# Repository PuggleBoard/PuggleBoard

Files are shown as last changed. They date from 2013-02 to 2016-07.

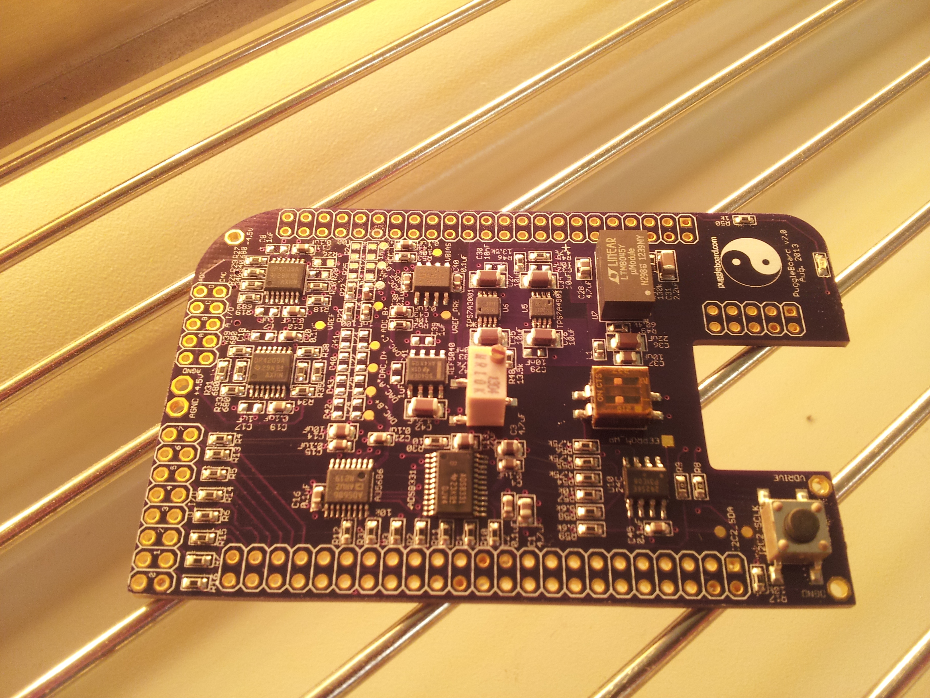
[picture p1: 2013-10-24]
art/PuggleBoard_2v1_reflow.jpg

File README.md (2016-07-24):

PuggleBoard
===

Note: The PuggleBoard project is no longer under active development as of 06/2016. For alternative low-cost electrophysiology options, please see <a href="http://github.com/rtxi/rtxi">RTXI</a> or <a href="http://github.com/open-ephys/">Open-Ephys</a>.

The [PuggleBoard] (http://puggleboard.com/) is an I/O interface that plugs into the BeagleBone Black's expansion headers and is controlled by <a href="https://github.com/PuggleBoard/PuggleDriver">PuggleDriver</a>.

To get started, please refer to the <a href="https://github.com/PuggleBoard/PuggleBoard/wiki">wiki</a>. If you encounter any trouble or have any questions, post them to the <a href="https://github.com/PuggleBoard/PuggleBoard/issues">issues section</a> and we'll help get you started.

Visit visit the <a href="http://puggleboard.com">Puggleboard</a> site for more information on Puggle and it's hardware/software components.

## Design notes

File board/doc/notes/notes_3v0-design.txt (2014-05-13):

I spoke with Edgar Brown about revision 2.1 and he gave a lot of helpful advice. Here is the summary of his comments.

1. [E] Use matched resistor arrays instead of discrete components

	> This is especially true for the onboard analog input/output stages.
	> Saves space
	> Individual resistors will introduce large mismatches unless you use relatively high tolerances. 
	> You can get 2% resistor arrays that have matched resistors down to 0.1% (these circuits are sensitive to matching, not to specific resistor values). 
	> Note that a 1% mismatch in that circuit can introduce a 300+ count mismatch on the output, more than twice the offset of the DAC itself. Not necessarily a problem, but something to keep in mind when using 16-bit DACs.
    > I see that the space is rather restricted, some resistor arrays (such as this one: http://www.digikey.com/product-detail/en/EXB-38V330JV/Y9330TR-ND/256513 ) could be used to open up some space around the connectors. One of those takes half the space than four 0603’s and are not that hard to solder.

2. [E] I am not sure of the specifics of the AD5686 or of the application, but in many bio-applications it is desirable to have simultaneously sampling ADCs and DACs (it considerably simplifies signal processing). I believe the LDAC line can serve this purpose, which here you have disabled.

	> Yes, that is the purpose of LDAC. We should dedicate an extra PRU pin to control LDAC. 
	> The ADS8331, however, does not allow simultaneous sampling. I'm not quite sure how this would simplify signal processing. 

3. [E] The schematics are harder to read than necessary as you used generic boxes for common items such as operational amplifiers. What is normally a quick pattern recognition task becomes a bit mental puzzle. It took me a minute to recognize a simple analog level shifter.

	> I will replace strange boxes with standard opamp symbols
	
X4. [E] Regarding the reset button. Why a reset button at all? it takes space and you would probably do it programmatically anyway. I am guessing that both the ADC and the DA can be reset via the SPI bus. If not a connection to a free I/O pin takes less space.

	> This is important to have for the sake of biologists. For instance, say they start inadvertantly electrolesioning an animal because they put a DC offset on a stimulating electrode. They panic. I want there to be a real button they can hit to make bad things stop. I actually use the reset switch quite a lot on Arduino boards, for instance.
	
?5. [E] I see no connection to the End of Conversion in the ADC. I am not sure if you need it, but it is normally required to drive the ADC at maximum speed.

	> My understanding is that this is used to signal an interupt indicating a conversion has taken place and the host processor can begin pulling data.
	> We have a fixed delay for conversions, so I'm not sure this will be helpful for us. Could be wrong here.
	
6. [E] What is the purpose of S1? wouldn’t it make more sense to select the address either programmatically or have it fixed for the board? That switch seems to take a lot of space for very little functionality. If the purpose is to be able to connect multiple boards together, I am not sure that your configuration of IO lines allows for that. A set of jumpers (resistor locations with 0-ohm resistors) could achieve the same thing with less space. (Also note that the parallel of R59 and R58 in multiple boards would quickly drive the I2C lines out of spec).

	> This is a requirement to produce a BeagleBoard 'cape' that conforms to BeagleBoard design requirments. Each BB is allowed up to four capes, defined by the position of the DIP switch, which must be selectable by the user. You are right that this could be done with solder joints or jumpers, but this is not the standard for other capes. Jumpers are a reasonable idea, but how much space will it really save?
	> In regard to R59/58 -- yes, but this again is what is recommended by BeagleBoard.org. Only 4 capes are allowed so I don't think that will be enough to load down the I2C line to the point where it no longer works.
	> Although our boards are not daisy-chainable, we want our board to conform to these requirments so it can be used with unrelated projects that use nonoverlapping GPIO pins -- e.g. a Wirless module or video capture.

7. [E]  Avoid connecting two pads directly, like pins 21 & 22 in U2. It makes it harder to spot soldering errors. Even when an outside company solders it, I have had to thoroughly inspect very carefully professionally soldered boards pin by pin to find soldering mistakes.

    > Good idea, will do.

8. [E] - Did you draw the INTAN wires by hand? Or is there some Eagle tool to match trace lengths now?
    
    > There is a tool. Its called the 'meander' tool.

9. [E] U7 is a major source of noise on top of AGND.I have to look at that IC more carefully, but I have a hunch that that is your main noise source on the whole board. The way AGND is organized around that IC guarantees that the noise it generates will find its way into all of the circuity.

    > [J] agree the U7 is certainly the most difficult to deal with from a design point. We need it to produce a negative power rail because we don't want the board to rely on a benchtop supply or batteries. I was really careful on the layout for that component (i.e. following the datasheet and eval board), and we actually do not see its switching transients leaking into the rest of the circuit in the current config. Of course, it could be producing less obviously correlated noise. I would really like to understand why this AGND pattern is no good. I am honestly at a loss sometimes with grounding patterns

10. [J] Our biggest, most obvious problem is definitely interference from the digital buses onto analog lines. 

    > [E] The connection of AGND to pin one on the right-side beaglebone connector might be the source of much of your digital noise. That creates a ground path for beaglebone digital signals through the AGND of your board. That is part of having just a single ‘point’ of connection between grounds. For space sake, and to reduce the adverse effects that simply disconnecting that ground might have on the switching noise from U7, It would be ok to have U7 in a separate GND domain directly connected to the beagle bone, with only L1 and C37 bridging the gap.

11. [E] I noticed that you have no anti-aliasing filters in place. You basically put a single pole at 1.6MHz for DACs that, I assume, will be sampling at a maximum of 125kS/s (this is already higher than the 1.25MHz bandwidth coming out of the op-amps). I know you are probably going for some flexibility, but this actually goes against your noise performance. You should at the very least move those filters down to 60kHz or so which should remove most of the problematic bandwidth. It might be advisable to change the amplifier architecture to incorporate 2-nd or 3-rd order filters there.

    > [J] Yeah, this is almost certainly true. At least the pole of the output filter should be below the opamp bandwidth...
    > One reason I don't want to put the pole all the way down at 60 kHz is that this prevents the user from generating fast square waves with the DAC. I suppose this is what the extra digital lines are for though?

12. Your switching frequency for the voltage converter is in the 700kHz range, which is already outside of the bandwidth of interest, but it can be easily aliased inside by lack of filtering (thus making it unrecognizable in a digital trace).

    > [J] Certainly true. I think this, and point 11, indicate that we need a lower frequency cutoff for the AA filtering

13. [E] I noticed that your ADC/DAC connector has no intervening grounds in it. Not much of a problem for the low-impedance DAC lines, but it can be an issue for the ADCs. The most common way to wire those is to have a row of grounds and a row of ‘active’ signals. That way the flat cable has a ground wire separating every signal from each other. As you have it, any noise in the DAC lines will capacitively and inductively couple back into the ADC lines. Add that to the lack of filtering and that is a clear path for noise.

    > [J] This is an easy change and we will certainly implement it. 

14. [E] Place the capacitors C5, C6, C9, C12 close to the ADC itself. That way any injected noise in those traces will have a direct path to the common node of the ADC itself. Alternatively connect the “COM” line from the ADC close to those capacitor's gnd, with a trace that closely follows those inputs.

    > [J] Thank you. This is the type of thing I never would have figured out on my own. Will certainly implement.

15. Replace the AD8032 and REF5040 with an MSOP package

    > Make sure to update BOM with (DK: AD8032ARMZ-REEL7CT-ND, MPN: AD8032ARMZ-REEL7)

16. You should have a mini-BNC or BNC sync out connection using a 50-ohm line driver or several paralled schmitt triggs with a characteristic 50-ohm out impedance. This will allow you to sync slave boards (e.g. the 64 channel version).

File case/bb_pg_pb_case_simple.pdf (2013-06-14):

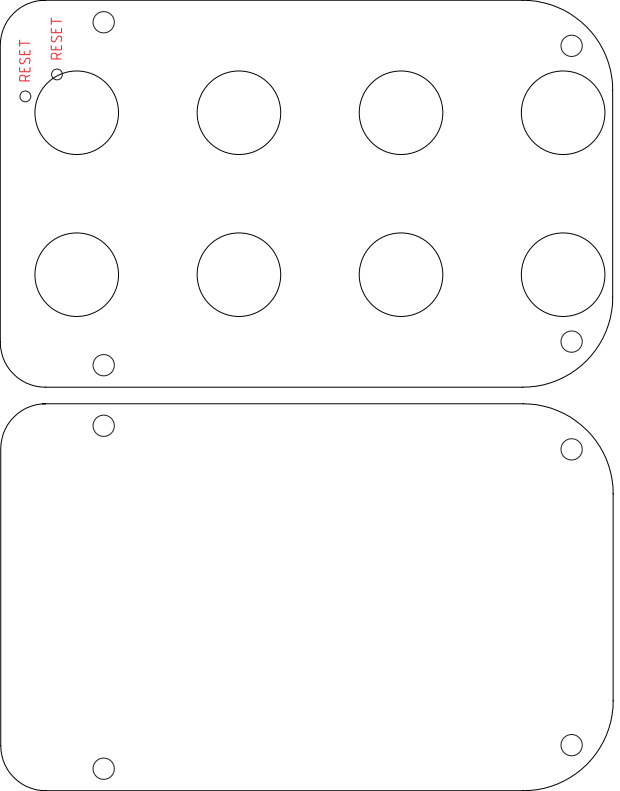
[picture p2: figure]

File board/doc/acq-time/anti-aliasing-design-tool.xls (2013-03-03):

 |  |  |  | Anti-Aliasing Filter Tool
Enter Converter Resolution: | 16 | bits
Enter Sample Rate: | 250000 | Hz
Nyquist Frequency: | 125000 | Hz
Enter Signal Bandwidth: | 20000 | Hz
Required Attenuation: | -98.08 | dB
Number of Filter Poles: | 4
Freq Factor | Frequency | Gain | Required Attenuation
0.0009765625 | 19.53125 | 0 | -98.08
0.001953125 | 39.0625 | 0 | -98.08
0.00390625 | 78.125 | 0 | -98.08
0.0078125 | 156.25 | 0 | -98.08
0.015625 | 312.5 | 0 | -98.08
0.03125 | 625 | 0 | -98.08
0.0625 | 1250 | 0 | -98.08
0.125 | 2500 | 0 | -98.08
0.25 | 5000 | 0 | -98.08
0.5 | 10000 | 0 | -98.08
1 | 20000 | 0 | -98.08
2 | 40000 | -24 | -98.08
4 | 80000 | -48 | -98.08
8 | 160000 | -72 | -98.08
16 | 320000 | -96 | -98.08
32 | 640000 | -120 | -98.08
64 | 1280000 | -144 | -98.08
128 | 2560000 | -168 | -98.08
256 | 5120000 | -192 | -98.08
512 | 10240000 | -216 | -98.08
1024 | 20480000 | -240 | -98.08
 | 250019.5312 | 0 | -98.08
 | 250039.0625 | 0 | -98.08
 | 250078.125 | 0 | -98.08
 | 250156.25 | 0 | -98.08
 | 250312.5 | 0 | -98.08
 | 250625 | 0 | -98.08
 | 251250 | 0 | -98.08
 | 252500 | 0 | -98.08
 | 255000 | 0 | -98.08
 | 260000 | 0 | -98.08
 | 270000 | 0 | -98.08
 | 290000 | -24 | -98.08
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

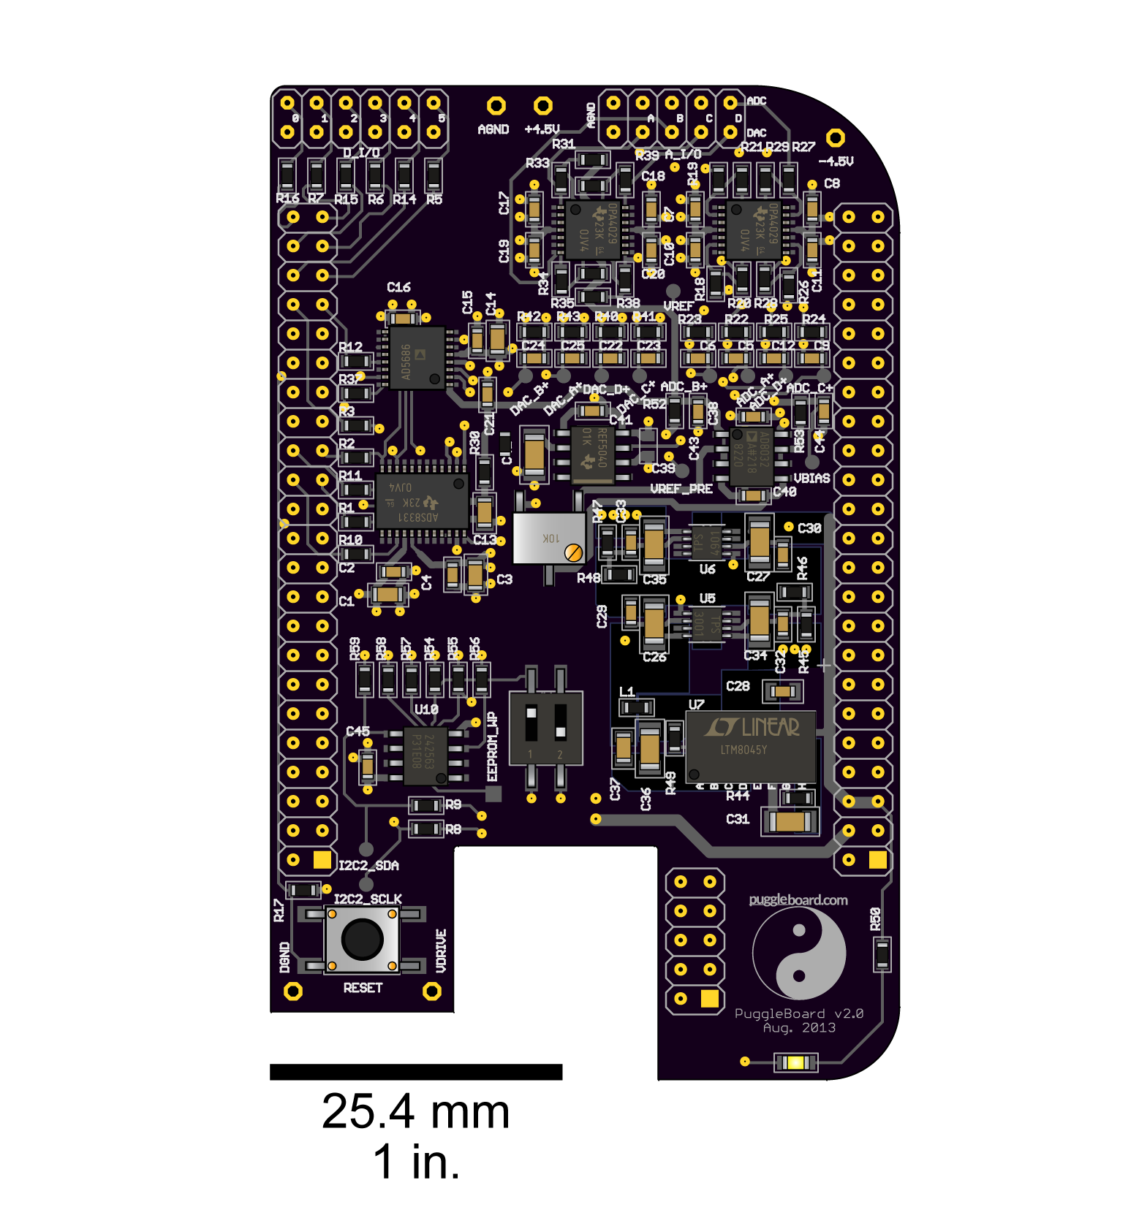
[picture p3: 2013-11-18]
art/PuggleBoard_2v1-02-01.png

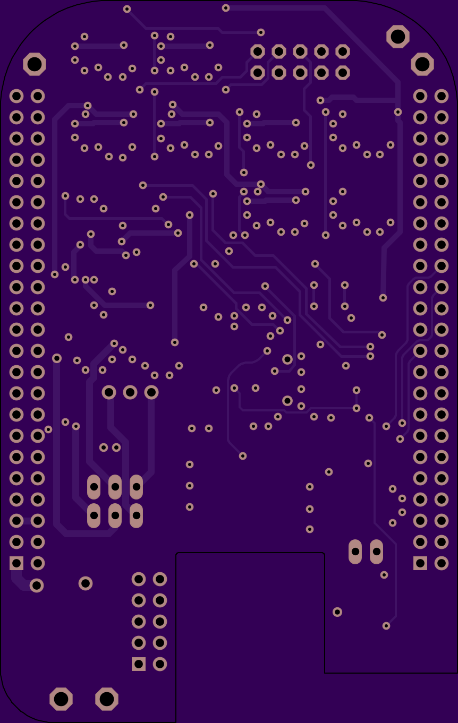
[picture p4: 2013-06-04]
art/PuggleBoard_OSHPark_Bottom.png

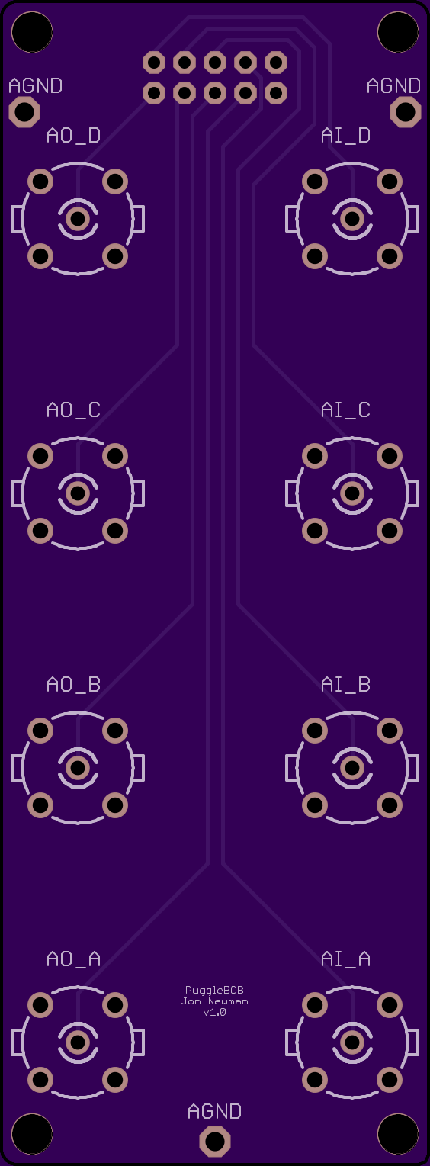
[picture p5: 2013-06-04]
bobs/bnc-bob/art/PuggleBOB_OSHPark_Top.png

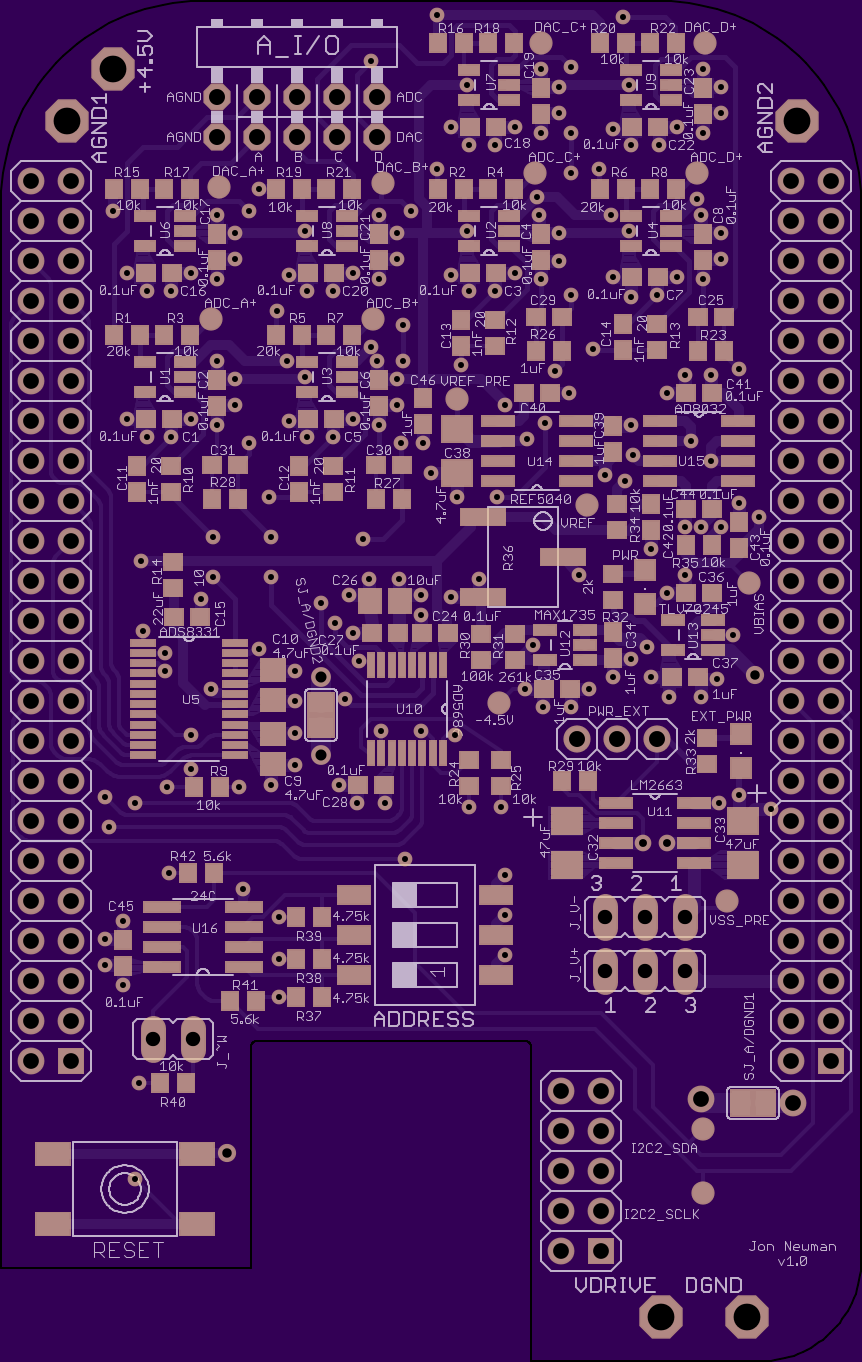
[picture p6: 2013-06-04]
art/PuggleBoard_OSHPark_Top.png

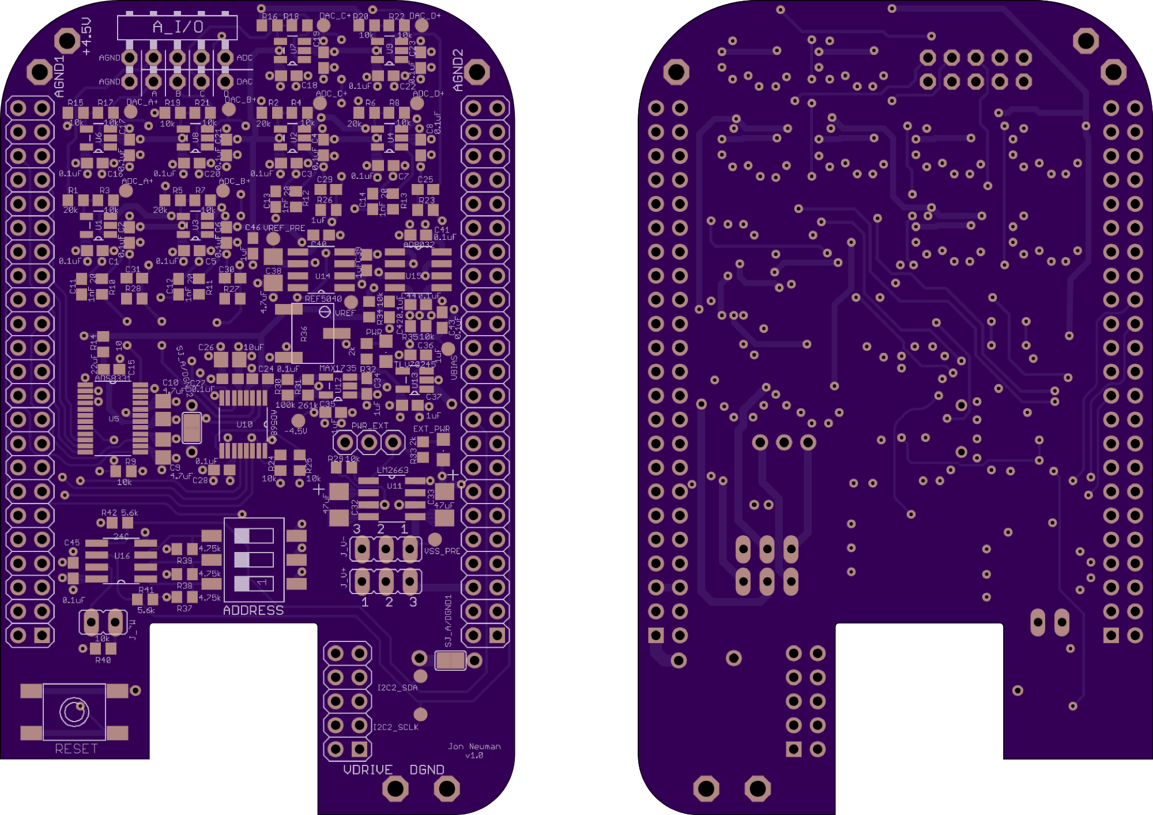
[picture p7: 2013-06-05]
art/PuggleBoard_OSHPark.png

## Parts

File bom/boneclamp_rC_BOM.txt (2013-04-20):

------------
1. POWER 
------------

DC-DC INVERTER (-5 VOLT OUTPUT):
--------------------------------
U1    N.A.    296-18729-1-ND    10-SON        1    DIGI-KEY    
C1    0.1uF   445-7558-1-ND     0805          1    DIGI-KEY    
C2    0.22uF  399-8053-1-ND     0805          1    DIGI-KEY  
C3    10pF    399-5567-1-ND     0805          1    DIGI-KEY    
C4    10uF    445-6857-1-ND     0805          1    DIGI-KEY  
C5    4.7uF   445-5973-1-ND     0805          4    DIGI-KEY   
C6    10nF    399-9154-1-ND     0805          1    DIGI-KEY  
C7    22nF    399-1163-1-ND     0805          1    DIGI-KEY  
C8    4.7nF   399-1155-1-ND     0805          1    DIGI-KEY  
R1    100k    P100KCCT-ND       0805          1    DIGI-KEY   
R2    150k    P150KCCT-ND       0805          1    DIGI-KEY  
R3    750k    P750KCCT-ND       0805          1    DIGI-KEY   
D1    N.A.    SL02-GS08CT-ND    DO-219AB      1    DIGI-KEY
L1    4.7uH   445-3235-1-ND     N.A.          1    DIGI-KEY  

DC-DC SWITCHED CAPACITOR VOLTAGE INVERTER (-VIN OUTPUT):
-----------------------------------------------------------
U1    N.A.    LM2663M/NOPB-ND PSOP-8          1    DIGI-KEY
C1,2  47uF    399-4714-1-ND   1206            2    DIGI-KEY

-5 VOLT LDO REGULATOR:
----------------------
U1    N.A.    LT1964ES5-5#TRMPBFCT-ND    10-SON      1    DIGI-KEY  
C1    1uF     399-1284-1-ND     0805          1    DIGI-KEY  
C2    10uF    445-6857-1-ND     0805          1    DIGI-KEY  
C3    10nF    399-9154-1-ND     0805          1     DIGI-KEY  

+4.75 VOLT LDO REGULATOR:
-------------------------
U1    N.A     296-28110-1-ND    SOT23-5       1   DIGI-KEY
C1,2  1uF     399-1284-1-ND     0805          2    DIGI-KEY  
L     N.A.    350-2044-1-ND     0805          1   DIGI-KEY

----------------------
2. SIGNAL CONDITIONING
----------------------

VADC BIAS:
----------
U1,2    N.A     AD8022ARZ-ND      8SOIC       2   DIGI-KEY

VDAC BIAS:
----------
U1,2    N.A     AD8022ARZ-ND      8SOIC       2   DIGI-KEY

----------------------
2. SIGNAL CONVERSION
----------------------

ADC:
----
C1,2    445-1316-1-ND     C1608X7R1E104K080AA   0603    DIGI-KEY

R1,2 	47k		A103211CT-ND	0805			2	DIGI-KEY

-----------------------
4. BEAGLEBONE INTERFACE
-----------------------

TEST1-4 N.A.    350-2041-1-ND 0805  4   DIGI-KEY
R1-4    2k      

RESET  N.A.     450-1129-ND     1   DIGI-KEY

----------------------
5. PROTOTYPE SUPPLIES
----------------------

BREAKOUT BOARDS
A1    N.A.    PA0063            20-QFN to DIP       1    PROTO-ADVANTAGE
A2    N.A.    PA0034            TSSOP-16 to DIP     1    PROTO-ADVANTAGE
A3    N.A.    PA0191            TSSOP-10 to DIP     1    PROTO-ADVANTAGE
A4    N.A.    PA0180            TSOT-6 to DIP       1    PROTO-ADVANTAGE

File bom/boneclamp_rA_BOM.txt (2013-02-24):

Jonathan P Newman
jnewman6 snail gatech dot edu

Revisions:
2013 01 24

********************************************************************************
                    T I N Y - C L A M P  C A P E  B. O. M.
********************************************************************************

Part No.            Description             Manufac.      Digikey No.           Quantity      

INTEGRATED CIRCUITS
--
AD5754              quad DAC                Analog        AD5724RBREZ-ND        1             
AD7656YSTZ-1        quad ADC                Analog        AD7656YSTZ-1-ND       1             
ADR421              2.5 Vref                Analog        ADR421BR-REEL7CT-ND   2             

PASSIVE COMPONENTS
--
44WR10KLFT7         10K Trimmer                 Bourns        987-1046-2-ND     x

for voltage refs:
10k trimmer
15k resistor
10 uF cap 
0.1 uF cap (2x)

for DAC:

for ADC:
1 uF cap (7x, max config, some of these are not nessesary)
2x schottky diode for supply pins (RB021VA90CT-ND)
6x 240 Ohm resistors in series with AI channels

Power reg:
2X logical level vreg for Vdig and Vanalog (dig)
+12 V vreg for Vdd (analog)
-12 V vreg for Vss (analog)
+5 V vreg for bone power (with required current ratings)

PV36P502C01B00      5K Trimmer                  Murata        490-2869-ND       1
44WR10KLFT7         10K Trimmer                 Bourns        987-1046-2-ND     x
AC07000001507JAC00  resistor, 0.15 ohm, 5%      Vishay        PPC7W.15CT-ND     1
PAC500002007FAC000  resistor, 0.2 ohm, 1%       Vishay        PPC5D.20CT-ND     1
AC07000003307JAC00  resistor, 0.33 ohm, 5%      Vishay        PPC7W.33CT-ND     1
NFR2500004707JR500  resistor, 0.47 ohm          Vishay        PPC.47ACT-ND      1
AC05000007507JAC00	resistor, 0.75 ohm					Vishay				PPC5W.75CT-ND			1
PR01000101200JR500  resistor, 120 ohm           Vishay        PPC120W-1CT-ND    1
PR01000102400JR500  resistor, 240 ohm           Vishay        PPC240W-1CT-ND    1
PR01000104700JR500  resistor, 470 ohm           Vishay        PPC470W-1CT-ND    1
PR01000101001JR500  resistor, 1 kohm            Vishay        PPC1.0KW-1CT-ND   1
PR01000101501JR500  resistor, 1.5 kohm          Vishay        PPC1.5KW-1CT-ND   1
PR01000105101JR500  resistor, 5.1 kohm          Vishay        PPC5.1KW-1CT-ND   2
PR01000101002JR500  resistor, 10 kohm           Vishay        PPC10KW-1CT-ND    2 
PR01000101004JR500  resistor, 1 Mohm            Vishay        PPC1.0MW-1CT-ND   1
RPE5C1H220J2K1Z03B  capacitor, 20 pf            Murata        490-3709-ND       1
RDEF51H104Z0K1C03B  capacitor, 100nf            Murata        490-5401-ND       4
ECA-1HM010          capacitor, 1 uF             Panasonic     P5174-ND          1  
ECA-1CM100          capacitor, 10 uF            Panasonic     P5134-ND          1
LTL1CHTBK4          On LED, 20 mA               lite-on       160-1602-ND       1

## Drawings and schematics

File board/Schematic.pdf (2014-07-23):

A

A

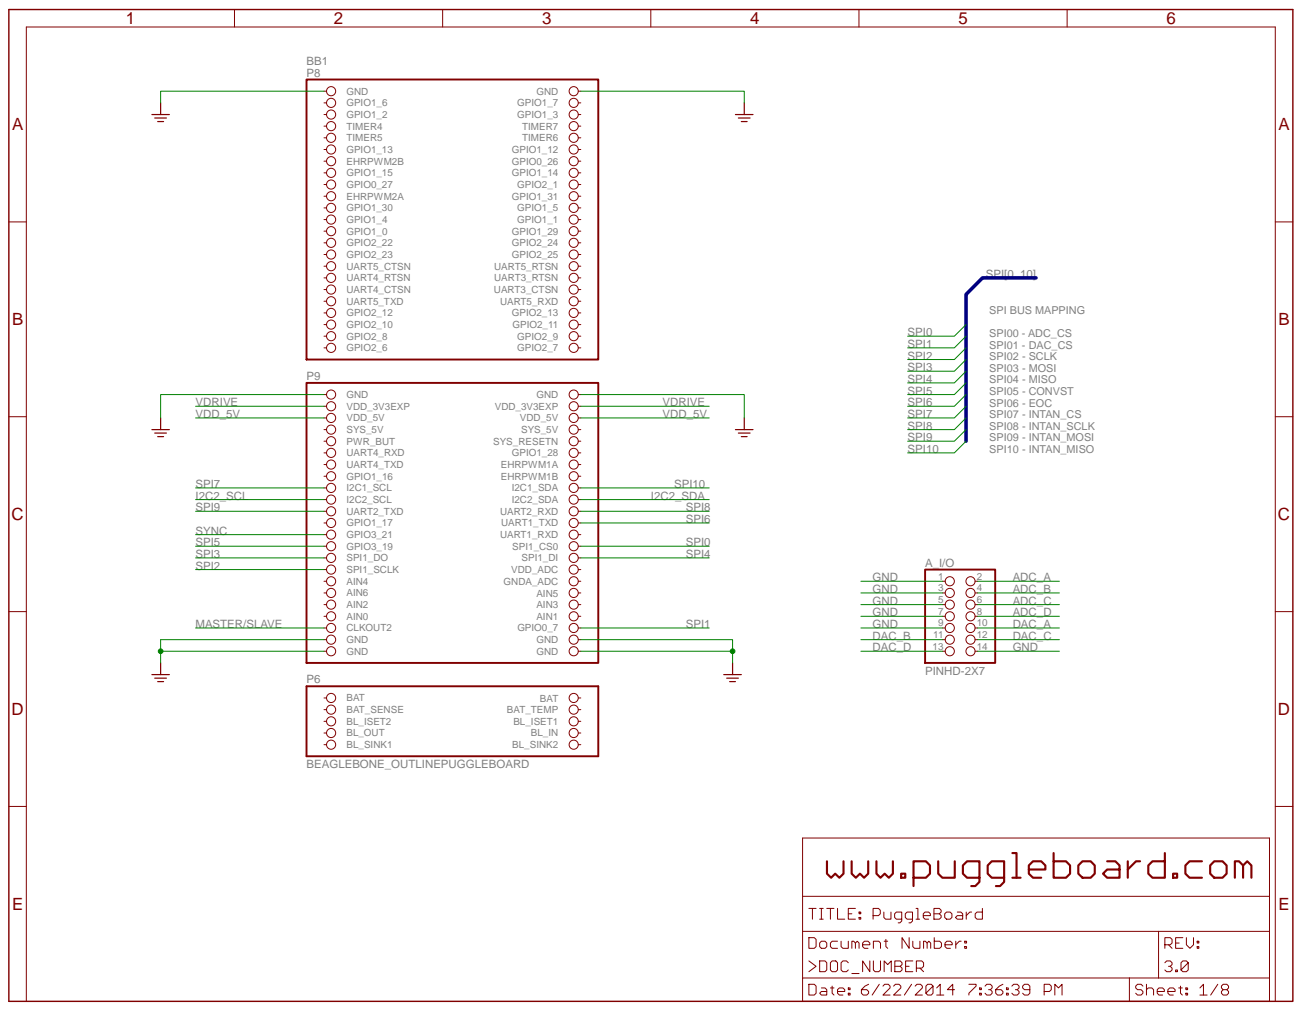
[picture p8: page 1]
SPI00 - ADC_CS SPI01 - DAC_CS SPI02 - SCLK SPI03 - MOSI SPI04 - MISO SPI05 - CONVST SPI06 - EOC SPI07 - INTAN_CS SPI08 - INTAN_SCLK SPI09 - INTAN_MOSI SPI10 - INTAN_MISO; BEAGLEBONE_OUTLINEPUGGLEBOARD; PINHD-2X7; GND; VDD_3V3EXP; VDD_5V; SYS_5V; PWR_BUT; SYS_RESETN; UART4_RXD; GPIO1_28; UART4_TXD; EHRPWM1A; GPIO1_16; EHRPWM1B; I2C1_SCL; I2C1_SDA; I2C2_SCL; I2C2_SDA; UART2_TXD; UART2_RXD; GPIO1_17; UART1_TXD; GPIO3_21; UART1_RXD; GPIO3_19; SPI1_CS0; SPI1_DO; SPI1_DI; SPI1_SCLK; VDD_ADC; AIN4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

SPI BUS MAPPING

A

A

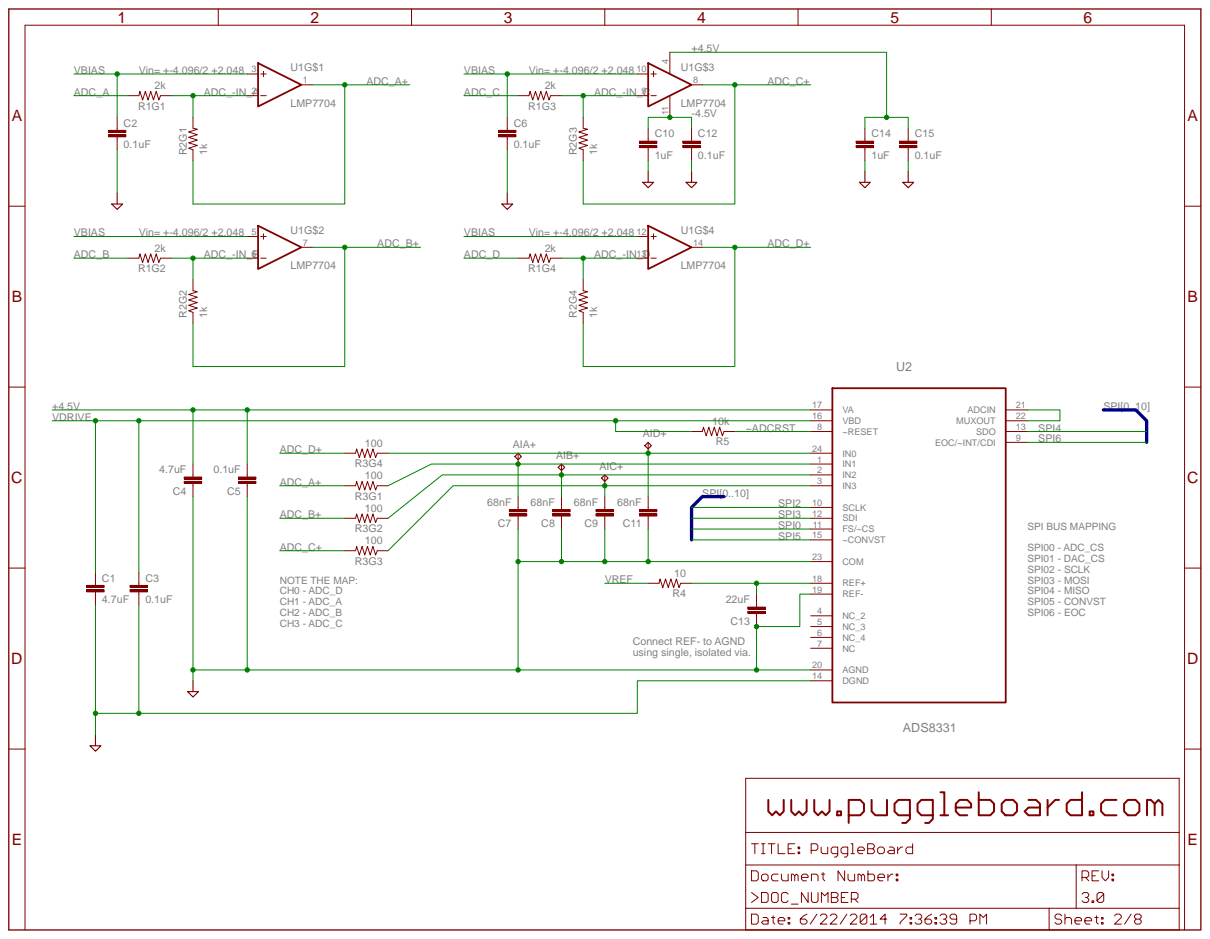
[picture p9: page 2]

Connect REF- to AGND
using single, isolated via.

A

A

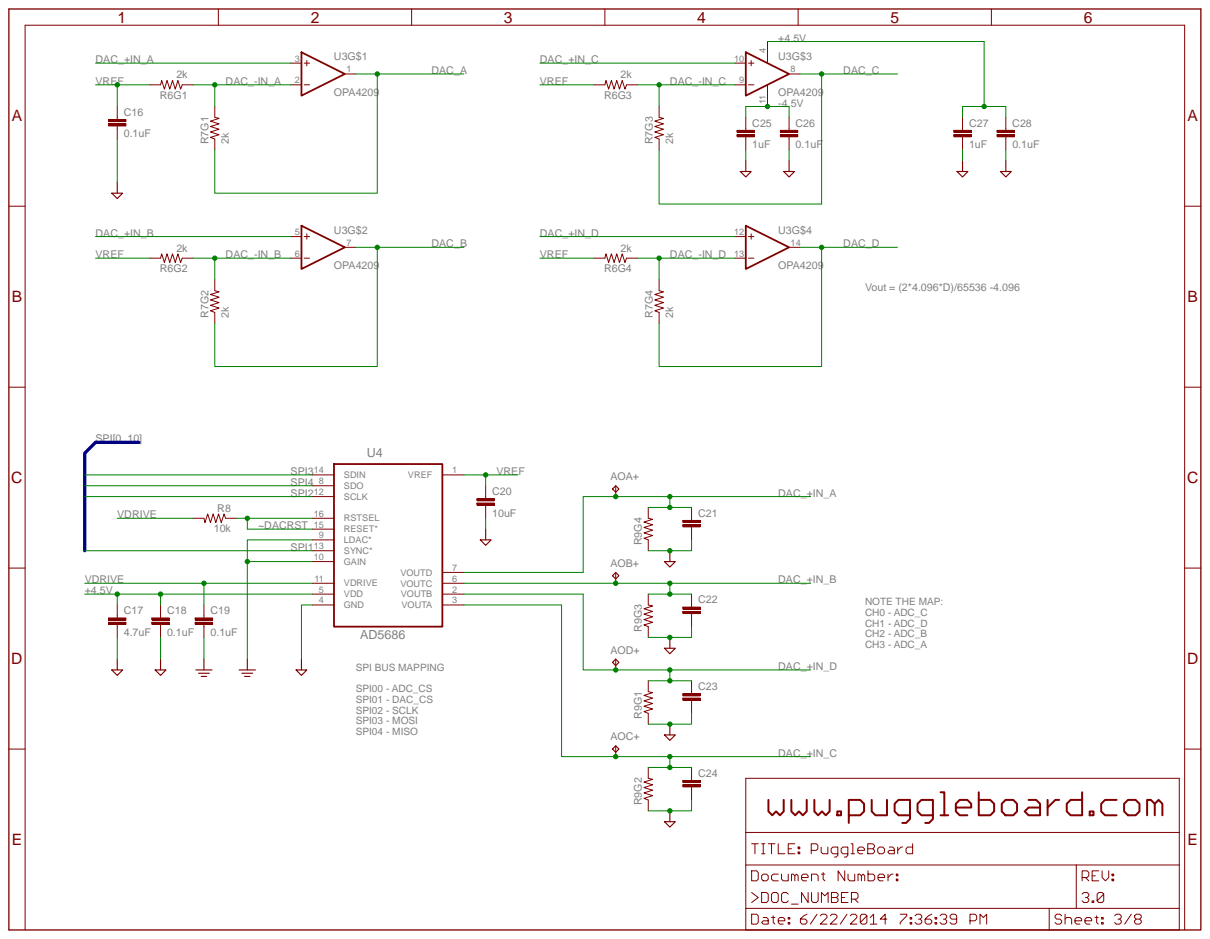
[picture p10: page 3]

A

A

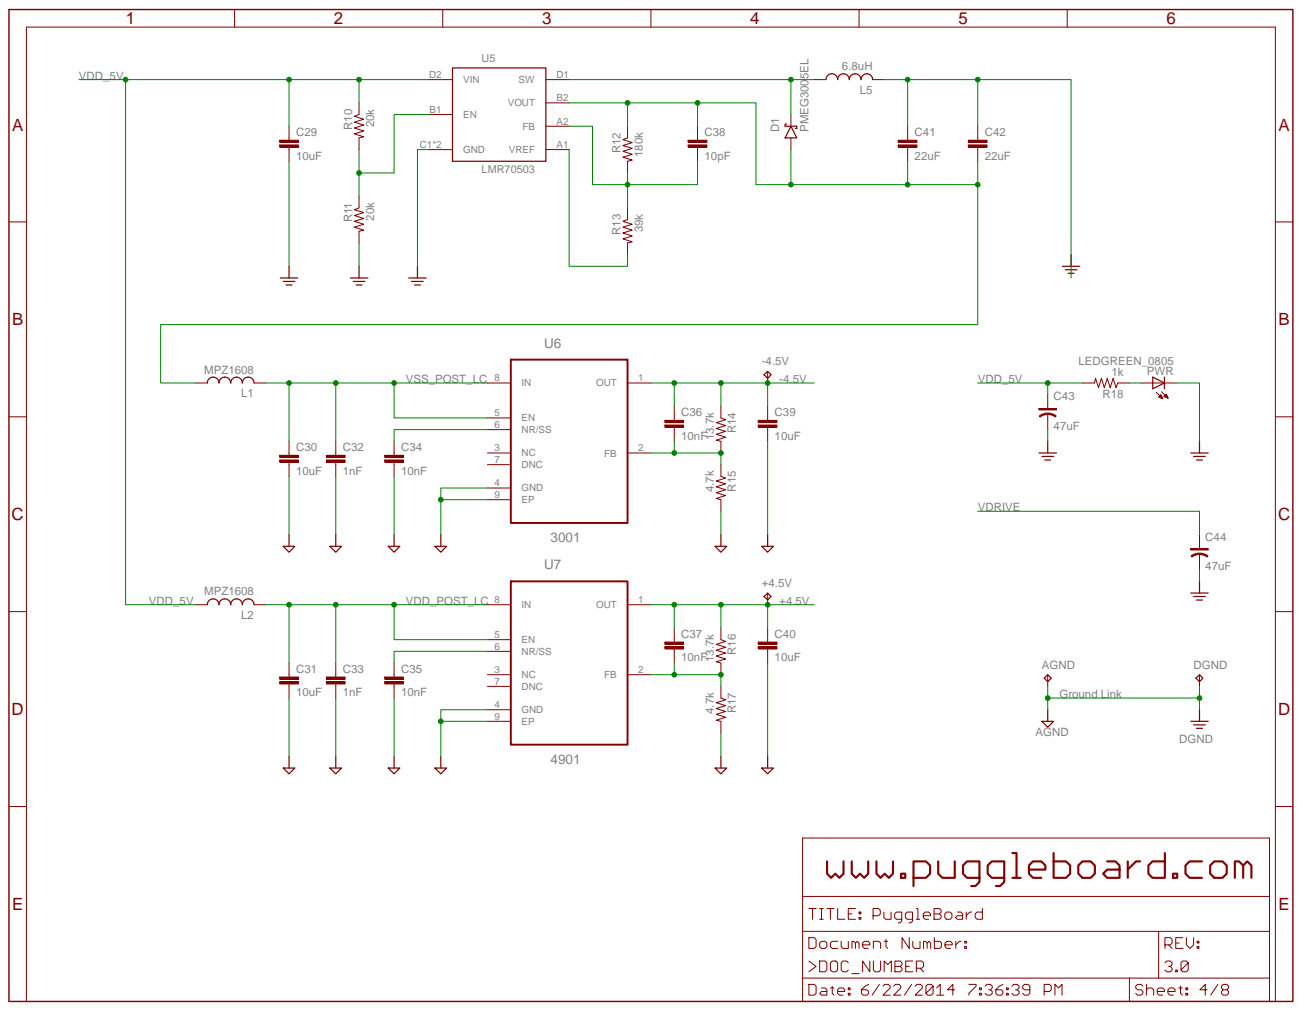
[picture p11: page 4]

A

A

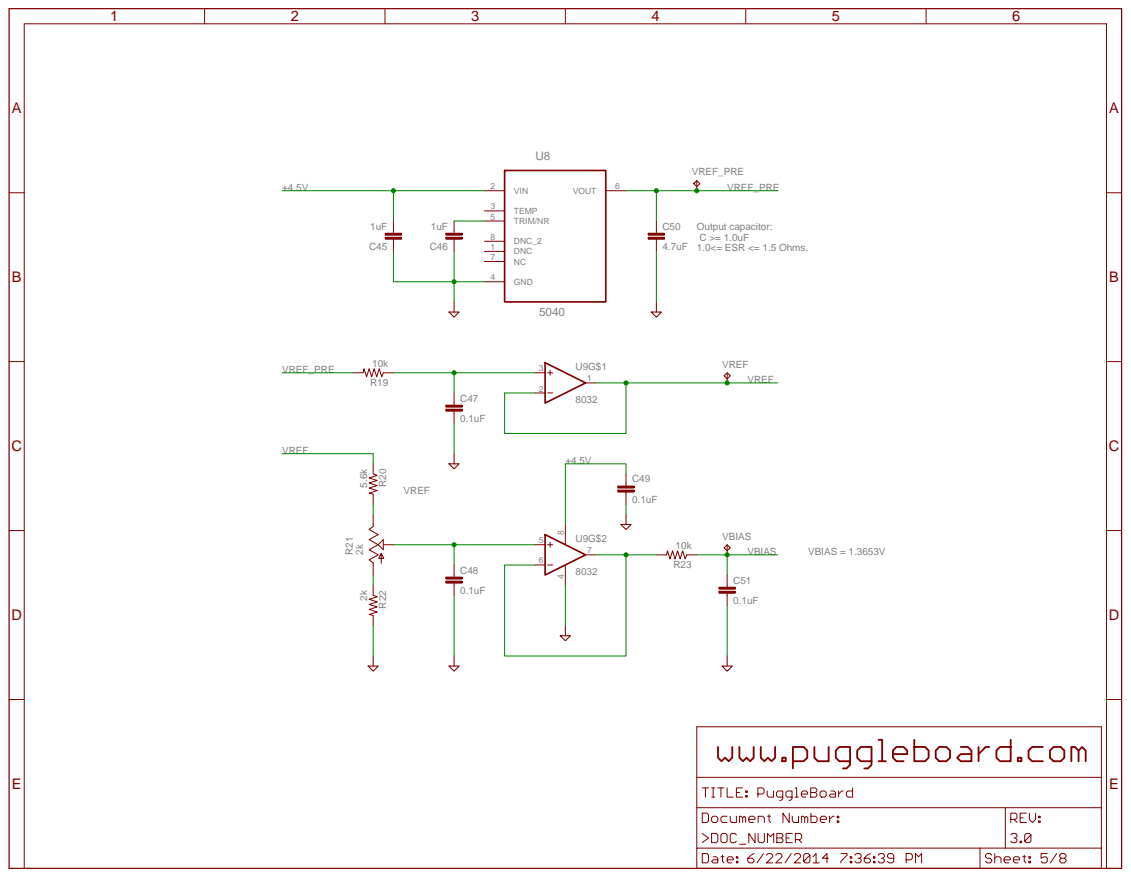
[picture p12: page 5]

A

A

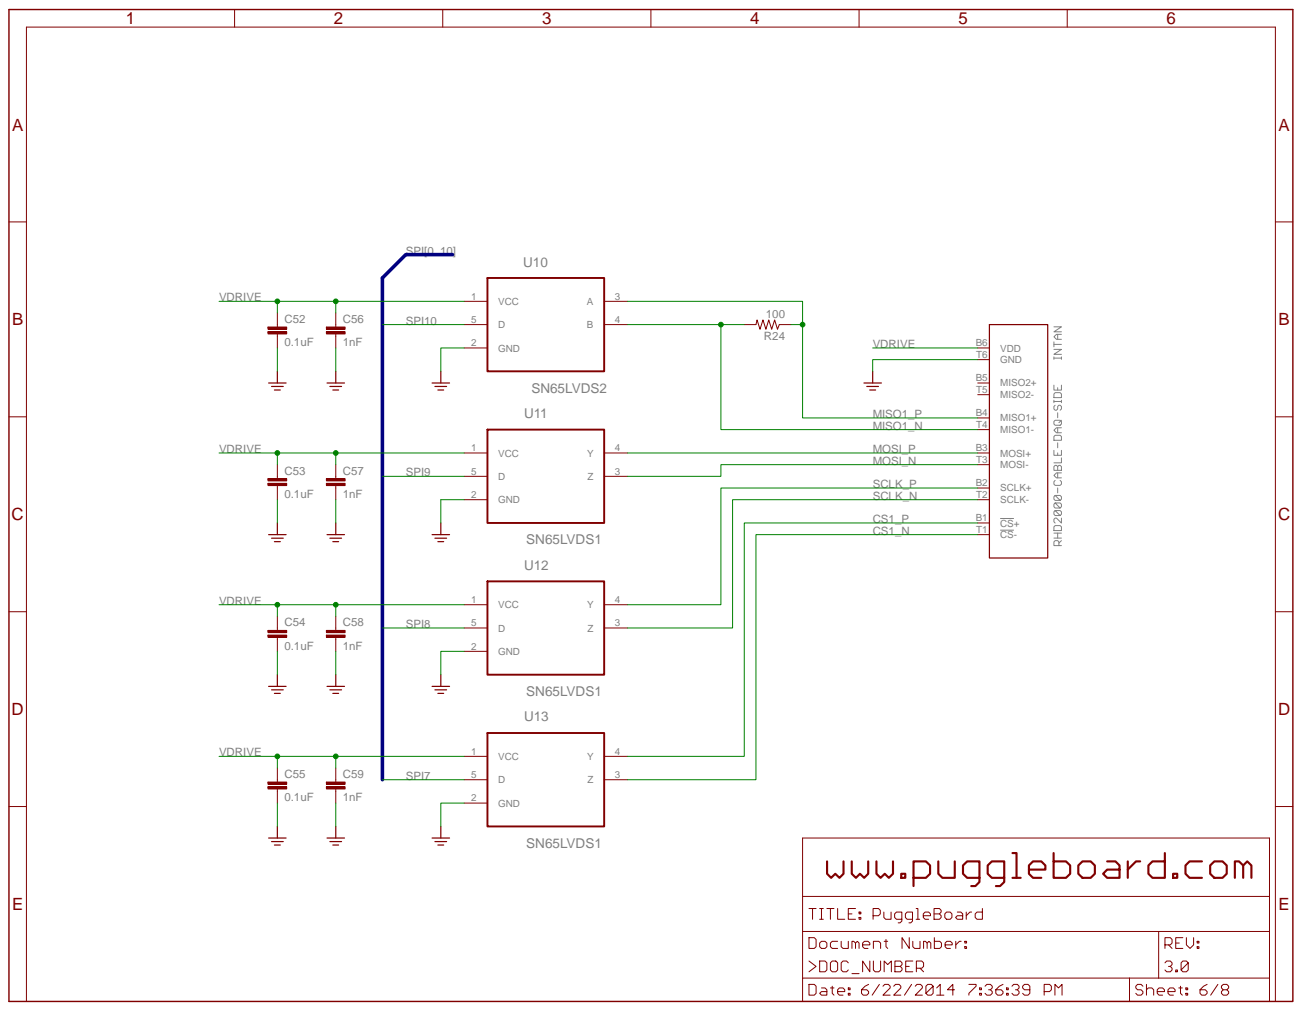
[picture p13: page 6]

A

A

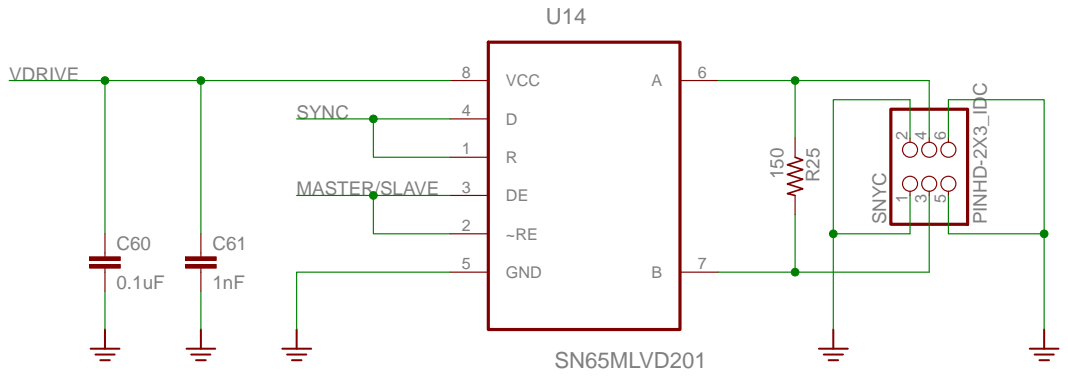
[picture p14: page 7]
SN65MLVD201; PINHD-2X3_IDC; VCC 8; GND 5; SNYC; SYNC; MASTER/SLAVE; VDRIVE

A

A

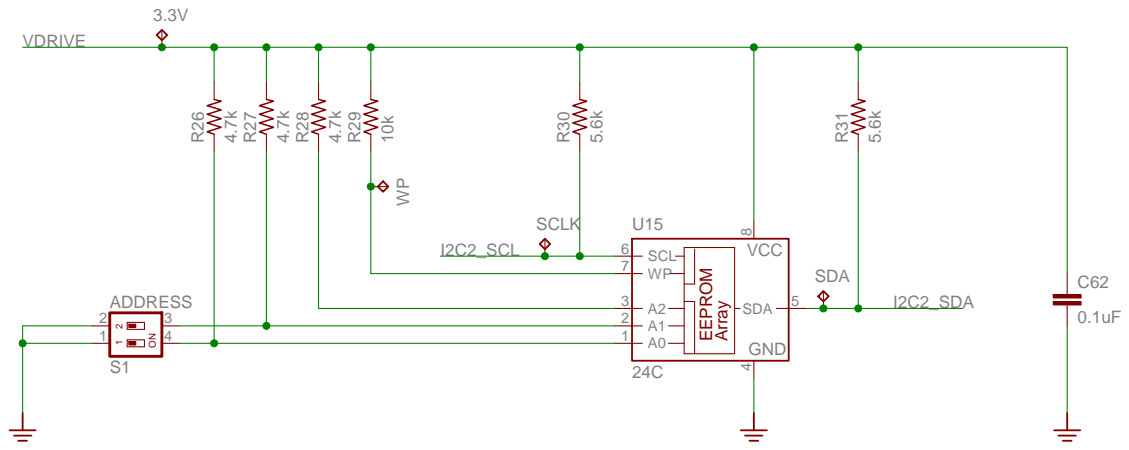
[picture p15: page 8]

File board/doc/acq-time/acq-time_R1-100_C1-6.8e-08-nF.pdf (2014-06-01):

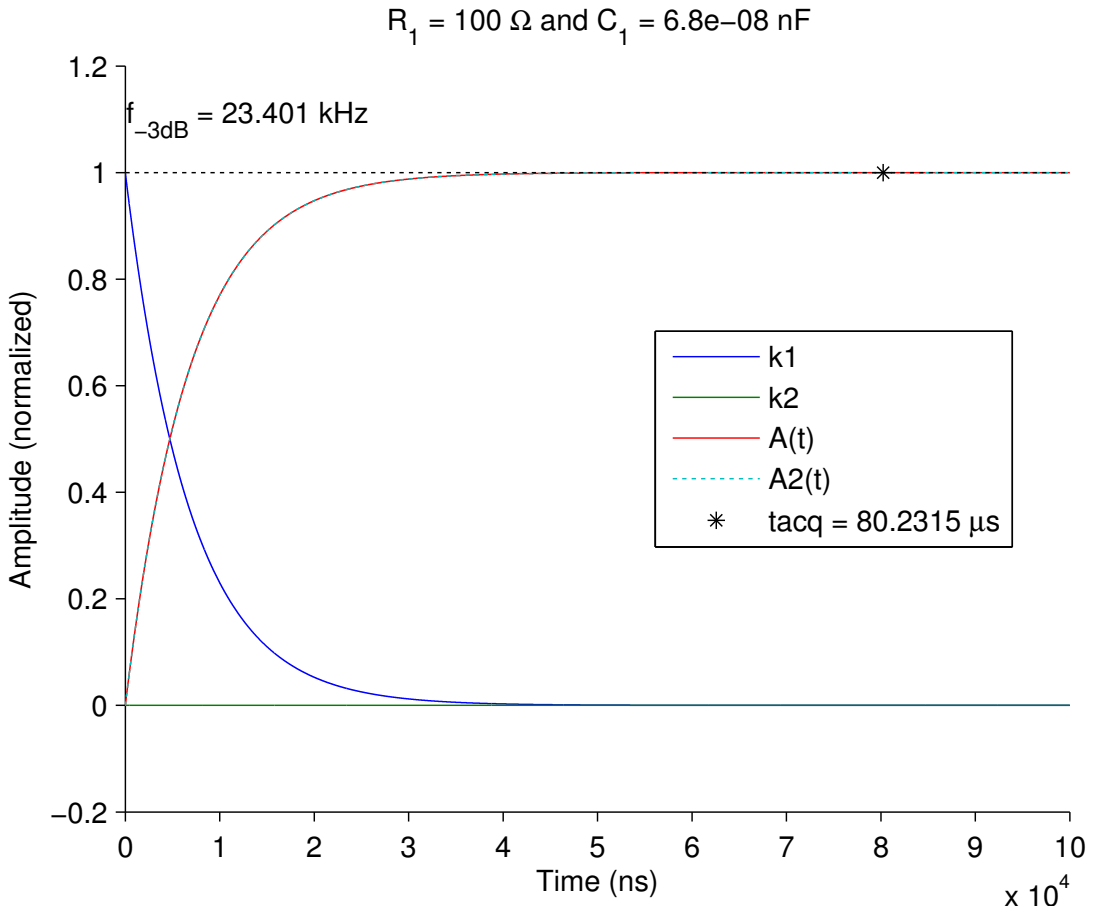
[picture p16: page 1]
Time (ns); Amplitude (normalized); = 100 Ω and C1; −3dB = 23.401 kHz; tacq = 80.2315 µs

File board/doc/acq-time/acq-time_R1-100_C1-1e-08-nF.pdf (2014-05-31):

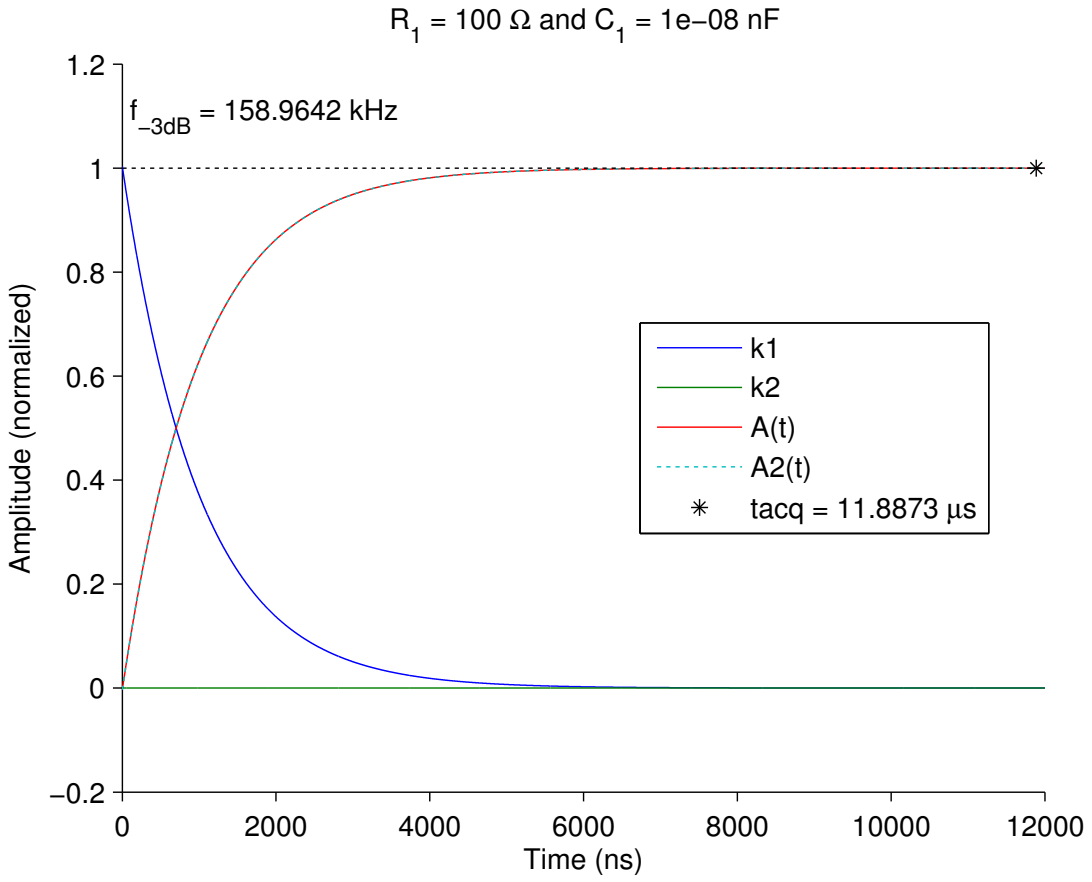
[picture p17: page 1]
Time (ns); Amplitude (normalized); = 100 Ω and C1; −3dB = 158.9642 kHz; tacq = 11.8873 µs

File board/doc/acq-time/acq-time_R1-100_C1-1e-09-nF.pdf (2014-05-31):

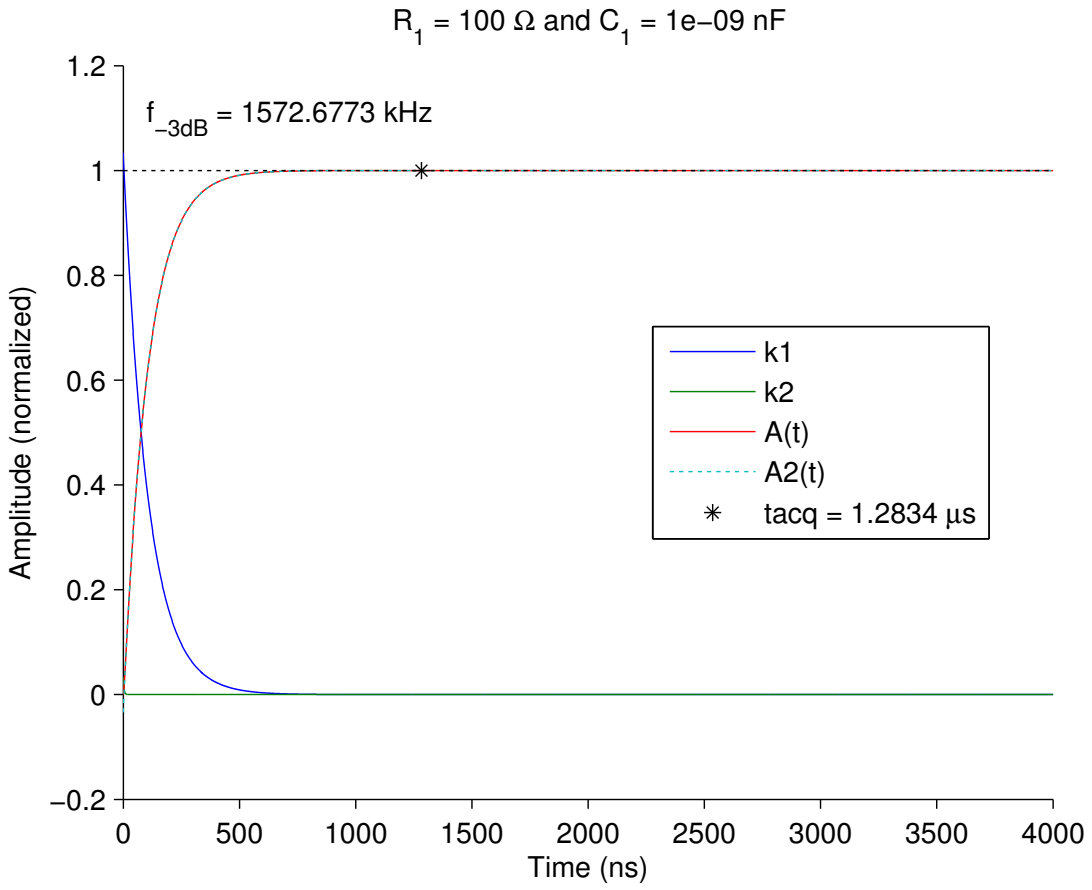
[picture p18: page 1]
Time (ns); Amplitude (normalized); = 100 Ω and C1; −3dB = 1572.6773 kHz; tacq = 1.2834 µs

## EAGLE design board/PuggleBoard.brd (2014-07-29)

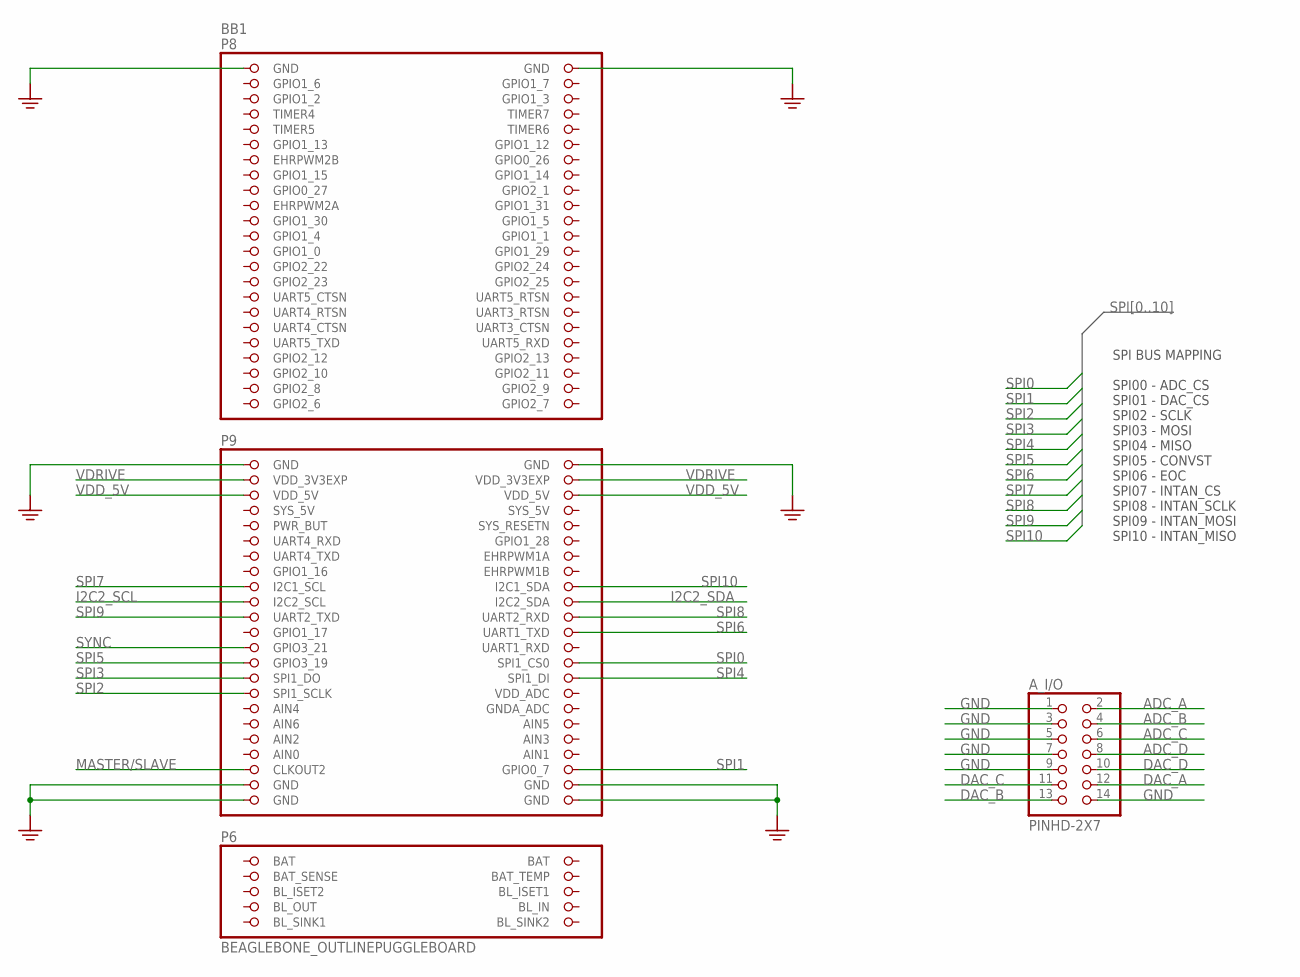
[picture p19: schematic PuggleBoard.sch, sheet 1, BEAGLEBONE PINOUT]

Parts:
A_I/O: PINHD-2X7; 2X07
BB1: BEAGLEBONE_OUTLINEPUGGLEBOARD; PUGGLEBOARD_SHIELD

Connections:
ADC_A: A_I/O.2; also elsewhere on the board
ADC_B: A_I/O.4; also elsewhere on the board
ADC_C: A_I/O.6; also elsewhere on the board
ADC_D: A_I/O.8; also elsewhere on the board
BAT_SENSE: BB1.95 (BAT_SENSE)
BL_IN: BB1.97 (BL_IN)
BL_OUT: BB1.100 (BL_OUT)
BL_SINK1: BB1.101 (BL_SINK1)
BL_SINK2: BB1.102 (BL_SINK2)
DAC_A: A_I/O.12; also elsewhere on the board
DAC_B: A_I/O.13; also elsewhere on the board
DAC_C: A_I/O.11; also elsewhere on the board
DAC_D: A_I/O.10; also elsewhere on the board
GND: A_I/O.1, A_I/O.3, A_I/O.5, A_I/O.7, A_I/O.9, A_I/O.14, BB1.1 (GND), BB1.2 (GND), BB1.47 (GND), BB1.48 (GND), BB1.89 (GND), BB1.90 (GND), BB1.91 (GND), BB1.92 (GND); also elsewhere on the board
I2C2_SCL: BB1.65 (I2C2_SCL); also elsewhere on the board
I2C2_SDA: BB1.66 (I2C2_SDA); also elsewhere on the board
MASTER/SLAVE: BB1.87 (CLKOUT2); also elsewhere on the board
SPI0: BB1.74 (SPI1_CS0); also elsewhere on the board
SPI1: BB1.88 (GPIO0_7); also elsewhere on the board
SPI2: BB1.77 (SPI1_SCLK); also elsewhere on the board
SPI3: BB1.75 (SPI1_DO); also elsewhere on the board
SPI4: BB1.76 (SPI1_DI); also elsewhere on the board
SPI5: BB1.73 (GPIO3_19); also elsewhere on the board
SPI6: BB1.70 (UART1_TXD); also elsewhere on the board
SPI7: BB1.63 (I2C1_SCL); also elsewhere on the board
SPI8: BB1.68 (UART2_RXD); also elsewhere on the board
SPI9: BB1.67 (UART2_TXD); also elsewhere on the board
SPI10: BB1.64 (I2C1_SDA); also elsewhere on the board
SYNC: BB1.71 (GPIO3_21); also elsewhere on the board
VDD_5V: BB1.51 (VDD_5V), BB1.52 (VDD_5V); also elsewhere on the board
VDRIVE: BB1.49 (VDD_3V3EXP), BB1.50 (VDD_3V3EXP); also elsewhere on the board

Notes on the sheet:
SPI BUS MAPPING SPI00 - ADC_CS SPI01 - DAC_CS SPI02 - SCLK SPI03 - MOSI SPI04 - MISO SPI05 - CONVST SPI06 - EOC SPI07 - INTAN_CS SPI08 - INTAN_SCLK SPI09 - INTAN_MOSI SPI10 - INTAN_MISO

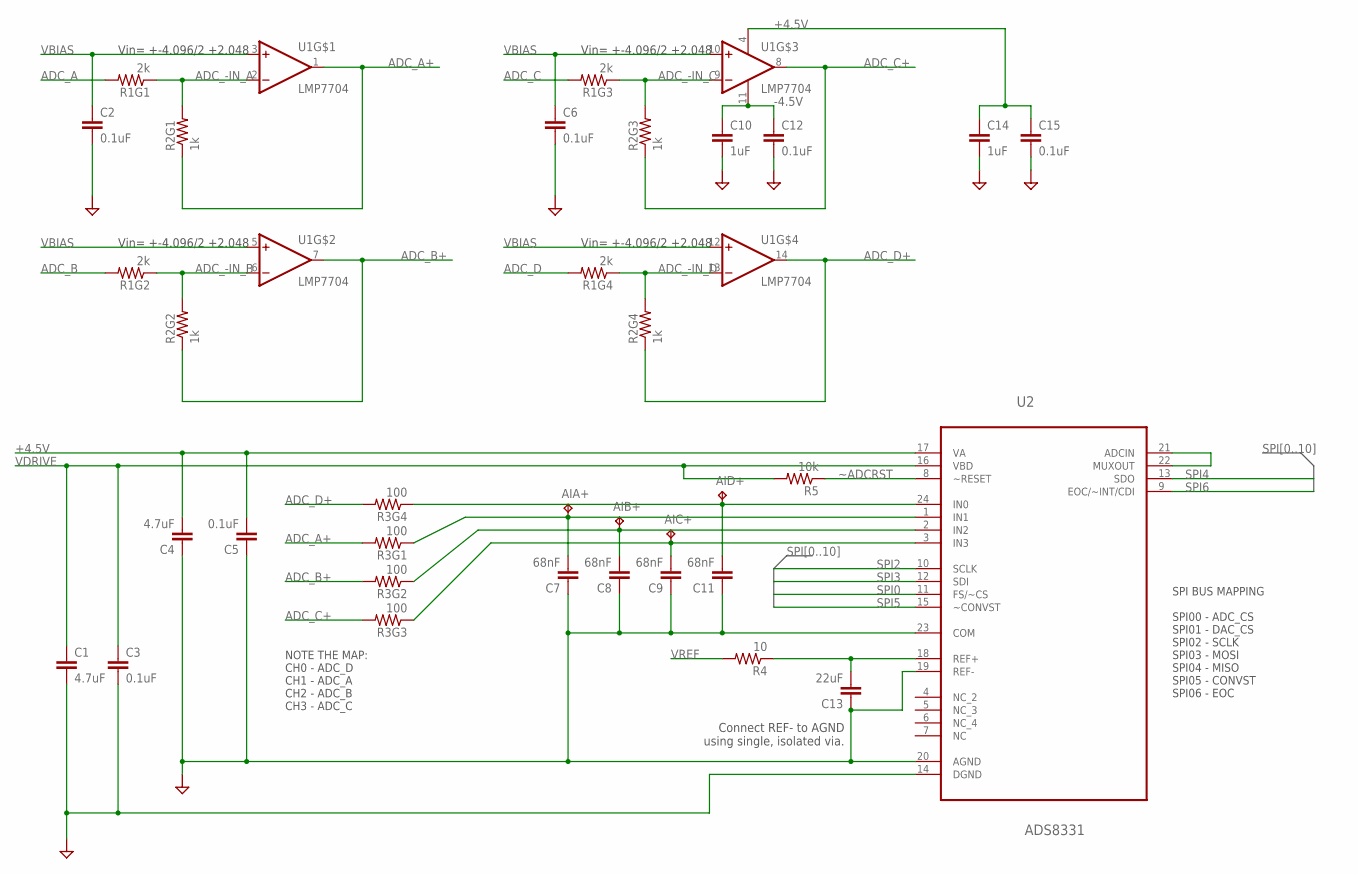
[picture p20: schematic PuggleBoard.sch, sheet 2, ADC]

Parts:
AIA+: TPB1,27; B1,27
AIB+: TPB1,27; B1,27
AIC+: TPB1,27; B1,27
AID+: TPB1,27; B1,27
C1, C4: 4.7uF; 0603
C2, C3, C5, C6, C12, C15: 0.1uF; 0603
C7, C8, C9, C11: 68nF; 0603
C10, C14: 1uF; 0603
C13: 22uF; 0805
R1: 2k; RX4_0612
R2: 1k; RX4_0612
R3: 100; RX4_0612
R4: 10; 0603
R5: 10k; 0603
U1: LMP7704; SOP65P640X120-14N-MOD
U2: ADS8331; SOP65P640X120-24N

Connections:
+4.5V: C4.2, C5.2, C14.1, C15.1, U1.4 (V+), U2.17 (VA); also elsewhere on the board
-4.5V: C10.1, C12.1, U1.11 (V-); also elsewhere on the board
ADC_-IN_A: R1.P1 (1), R2.P2 (2), U1.2 (-IN)
ADC_-IN_B: R1.P3 (1), R2.P4 (2), U1.6 (-IN)
ADC_-IN_C: R1.P5 (1), R2.P6 (2), U1.9 (-IN)
ADC_-IN_D: R1.P7 (1), R2.P8 (2), U1.13 (-IN)
ADC_A: R1.P2 (2); also elsewhere on the board
ADC_A+: R2.P1 (1), R3.P2 (2), U1.1 (OUT)
ADC_B: R1.P4 (2); also elsewhere on the board
ADC_B+: R2.P3 (1), R3.P4 (2), U1.7 (OUT)
ADC_C: R1.P6 (2); also elsewhere on the board
ADC_C+: R2.P5 (1), R3.P6 (2), U1.8 (OUT)
ADC_D: R1.P8 (2); also elsewhere on the board
ADC_D+: R2.P7 (1), R3.P8 (2), U1.14 (OUT)
GND: C1.2, C2.2, C3.2, C4.1, C5.1, C6.2, C7.1, C8.1, C9.1, C10.2, C11.1, C12.2, C13.1, C14.2, C15.2, U2.14 (DGND), U2.19 (REF-), U2.20 (AGND), U2.23 (COM); also elsewhere on the board
unnamed: U2.21 (ADCIN), U2.22 (MUXOUT)
unnamed: C13.2, R4.1, U2.18 (REF+)
unnamed: AIA+.TP, C7.2, R3.P1 (1), U2.1 (IN1)
unnamed: AIB+.TP, C8.2, R3.P3 (1), U2.2 (IN2)
unnamed: AIC+.TP, C9.2, R3.P5 (1), U2.3 (IN3)
unnamed: AID+.TP, C11.2, R3.P7 (1), U2.24 (IN0)
SPI0: U2.11 (FS/~CS); also elsewhere on the board
SPI2: U2.10 (SCLK); also elsewhere on the board
SPI3: U2.12 (SDI); also elsewhere on the board
SPI4: U2.13 (SDO); also elsewhere on the board
SPI5: U2.15 (~CONVST); also elsewhere on the board
SPI6: U2.9 (EOC/~INT/CDI); also elsewhere on the board
VBIAS: C2.1, C6.1, U1.3 (+IN), U1.5 (+IN), U1.10 (+IN), U1.12 (+IN); also elsewhere on the board
VDRIVE: C1.1, C3.1, R5.2, U2.16 (VBD); also elsewhere on the board
VREF: R4.2; also elsewhere on the board
~ADCRST: R5.1, U2.8 (~RESET)

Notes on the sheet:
Connect REF- to AGND using single, isolated via.
Vin= +-4.096/2 +2.048
SPI BUS MAPPING SPI00 - ADC_CS SPI01 - DAC_CS SPI02 - SCLK SPI03 - MOSI SPI04 - MISO SPI05 - CONVST SPI06 - EOC
NOTE THE MAP: CH0 - ADC_D CH1 - ADC_A CH2 - ADC_B CH3 - ADC_C

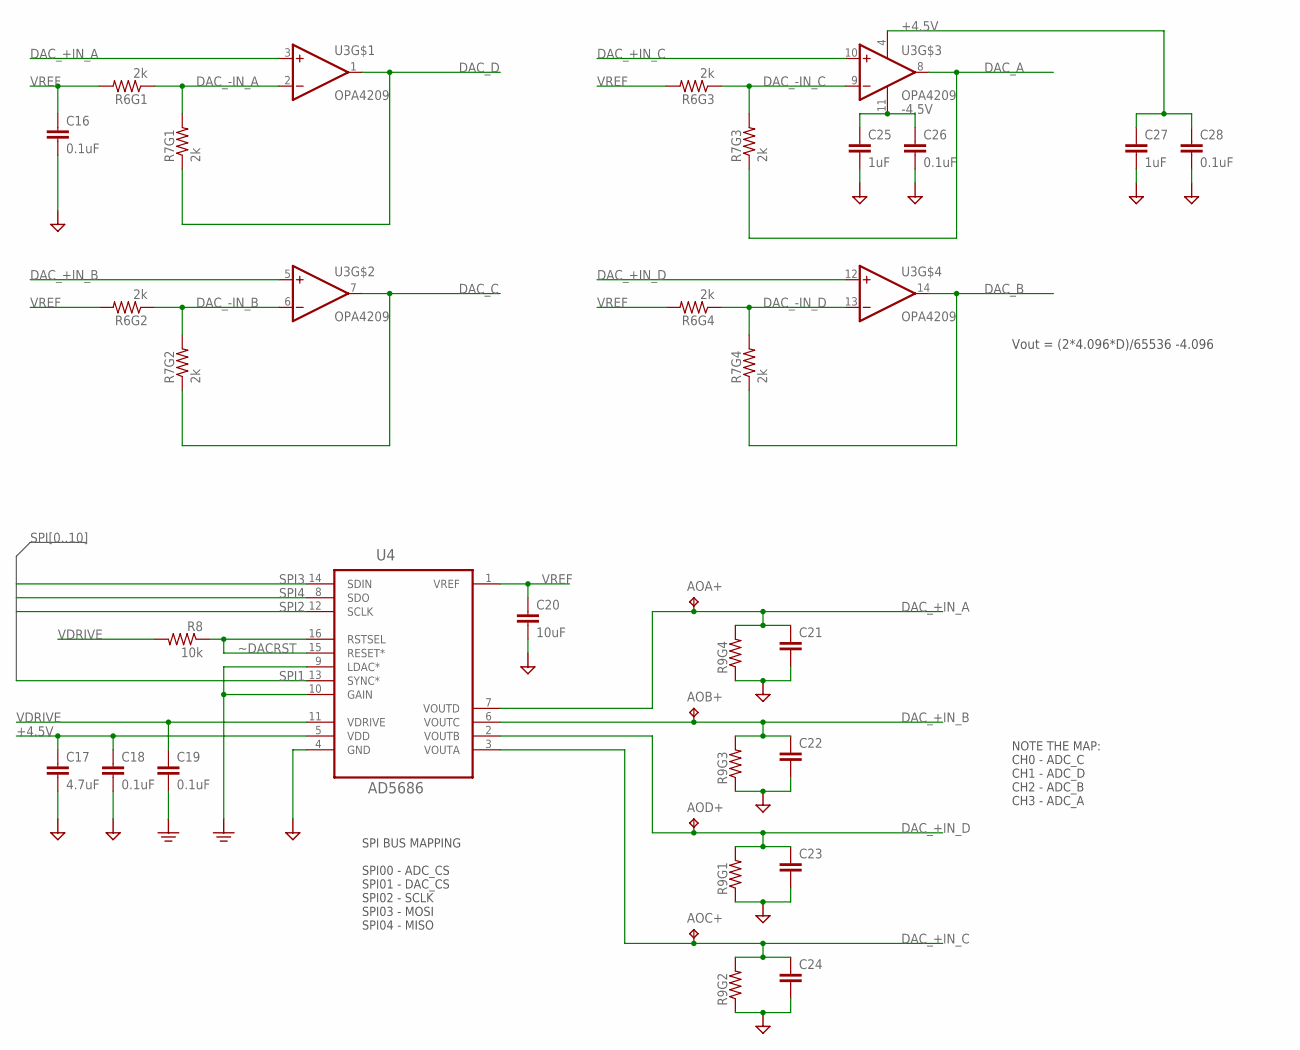
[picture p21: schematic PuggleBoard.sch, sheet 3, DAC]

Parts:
AOA+: TPB1,27; B1,27
AOB+: TPB1,27; B1,27
AOC+: TPB1,27; B1,27
AOD+: TPB1,27; B1,27
C16, C18, C19, C26, C28: 0.1uF; 0603
C17: 4.7uF; 0603
C20: 10uF; 0805
C21, C22, C23, C24: C_0603; 0603
C25, C27: 1uF; 0603
R6, R7: 2k; RX4_0612
R8: 10k; 0603
R9: RX4_0612
U3: OPA4209; SOP65P640X120-14N-MOD
U4: AD5686; MO-153-AB

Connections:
+4.5V: C17.1, C18.1, C27.1, C28.1, U3.4 (V+), U4.5 (VDD); also elsewhere on the board
-4.5V: C25.1, C26.1, U3.11 (V-); also elsewhere on the board
DAC_+IN_A: AOA+.TP, C21.1, R9.P8 (2), U3.3 (+IN), U4.7 (VOUTD)
DAC_+IN_B: AOB+.TP, C22.1, R9.P6 (2), U3.5 (+IN), U4.6 (VOUTC)
DAC_+IN_C: AOC+.TP, C24.1, R9.P4 (2), U3.10 (+IN), U4.3 (VOUTA)
DAC_+IN_D: AOD+.TP, C23.1, R9.P2 (2), U3.12 (+IN), U4.2 (VOUTB)
DAC_-IN_A: R6.P1 (1), R7.P2 (2), U3.2 (-IN)
DAC_-IN_B: R6.P3 (1), R7.P4 (2), U3.6 (-IN)
DAC_-IN_C: R6.P5 (1), R7.P6 (2), U3.9 (-IN)
DAC_-IN_D: R6.P7 (1), R7.P8 (2), U3.13 (-IN)
DAC_A: R7.P5 (1), U3.8 (OUT); also elsewhere on the board
DAC_B: R7.P7 (1), U3.14 (OUT); also elsewhere on the board
DAC_C: R7.P3 (1), U3.7 (OUT); also elsewhere on the board
DAC_D: R7.P1 (1), U3.1 (OUT); also elsewhere on the board
GND: C16.2, C17.2, C18.2, C19.2, C20.2, C21.2, C22.2, C23.2, C24.2, C25.2, C26.2, C27.2, C28.2, R9.P1 (1), R9.P3 (1), R9.P5 (1), R9.P7 (1), U4.4 (GND), U4.9 (LDAC*), U4.10 (GAIN); also elsewhere on the board
SPI1: U4.13 (SYNC*); also elsewhere on the board
SPI2: U4.12 (SCLK); also elsewhere on the board
SPI3: U4.14 (SDIN); also elsewhere on the board
SPI4: U4.8 (SDO); also elsewhere on the board
VDRIVE: C19.1, R8.2, U4.11 (VDRIVE); also elsewhere on the board
VREF: C16.1, C20.1, R6.P2 (2), R6.P4 (2), R6.P6 (2), R6.P8 (2), U4.1 (VREF); also elsewhere on the board
~DACRST: R8.1, U4.15 (RESET*), U4.16 (RSTSEL)

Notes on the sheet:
Vout = (2*4.096*D)/65536 -4.096
SPI BUS MAPPING SPI00 - ADC_CS SPI01 - DAC_CS SPI02 - SCLK SPI03 - MOSI SPI04 - MISO
NOTE THE MAP: CH0 - ADC_C CH1 - ADC_D CH2 - ADC_B CH3 - ADC_A

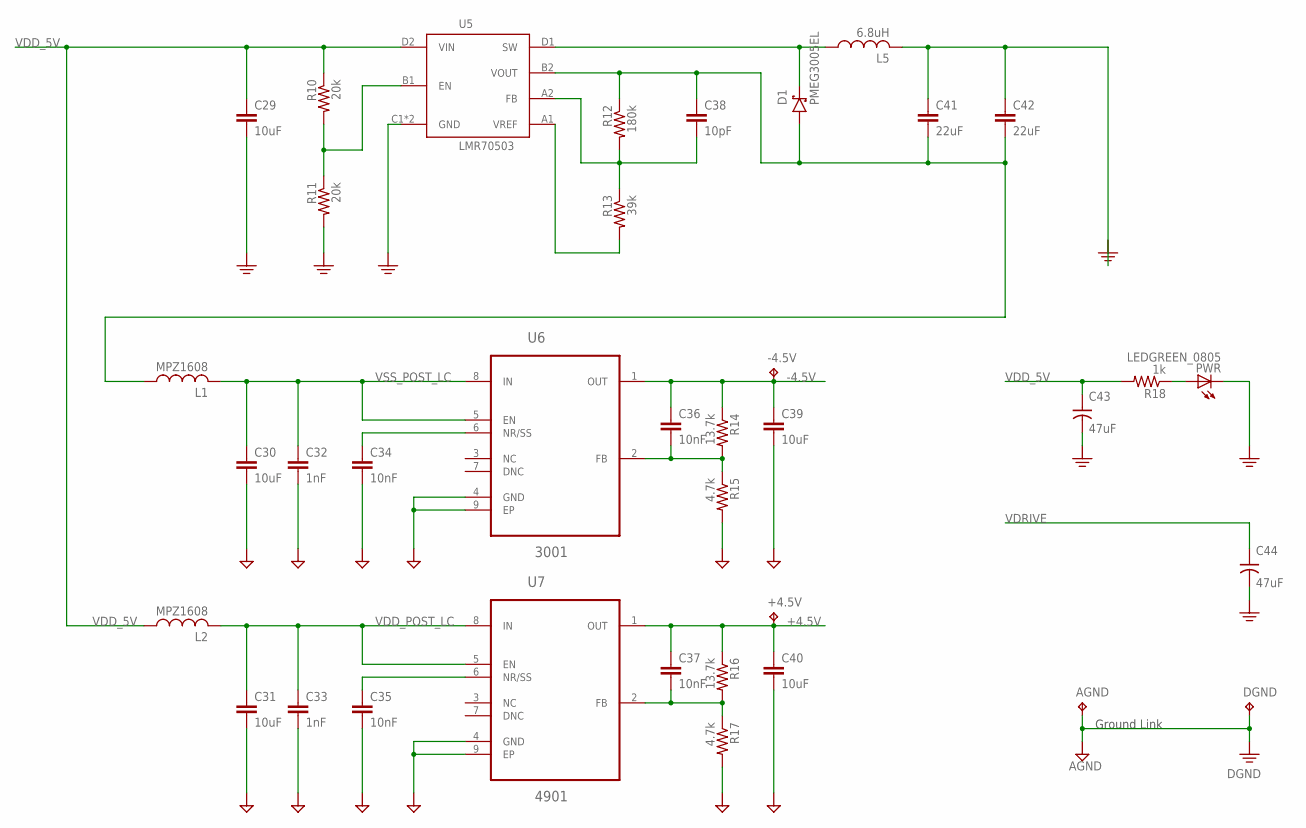
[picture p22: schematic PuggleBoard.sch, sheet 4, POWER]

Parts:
+4.5V: TPPAD1-17; P1-17
-4.5V: TPPAD1-17; P1-17
AGND: TPPAD1-17; P1-17
C29: 10uF; 0603
C30, C31, C39, C40: 10uF; 1206
C32, C33: 1nF; 0603
C34, C35, C36, C37: 10nF; 0603
C38: 10pF; 0402
C41, C42: 22uF; 0603
C43, C44: 47uF; 153CLV-0807
D1: PMEG3005EL; SOD882
DGND: TPPAD1-17; P1-17
L1, L2: MPZ1608; 0603
L5: 6.8uH; VLS2012E
PWR: LEDGREEN_0805; CHIP-LED0805
R10, R11: 20k; 0402
R12: 180k; 0402
R13: 39k; 0402
R14, R16: 13.7k; 0603
R15, R17: 4.7k; 0603
R18: 1k; 0603
U5: LMR70503; 8BGA
U6: 3001; SOP65P490X110-9N
U7: 4901; SOP65P490X110-9N

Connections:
+4.5V: +4.5V.TP, C37.1, C40.1, R16.1, U7.1 (OUT); also elsewhere on the board
-4.5V: -4.5V.TP, C36.1, C39.1, R14.1, U6.1 (OUT); also elsewhere on the board
AGND1: C37.2, R16.2, R17.1, U7.2 (FB)
AGND2: C36.2, R14.2, R15.1, U6.2 (FB)
GND: AGND.TP, C29.2, C30.2, C31.2, C32.2, C33.2, C34.2, C35.2, C39.2, C40.2, C41.1, C42.1, C43.-, C44.-, DGND.TP, L5.2, PWR.C, R11.2, R15.2, R17.2, U5.C1 (GND), U5.C2 (GND), U6.4 (GND), U6.9 (EP), U7.4 (GND), U7.9 (EP); also elsewhere on the board
unnamed: C35.1, U7.6 (NR/SS)
unnamed: C34.1, U6.6 (NR/SS)
unnamed: R10.2, R11.1, U5.B1 (EN)
unnamed: C38.2, R12.2, R13.1, U5.A2 (FB)
unnamed: PWR.A, R18.1
unnamed: R13.2, U5.A1 (VREF)
SW: D1.C, L5.1, U5.D1 (SW)
VDD_5V: C29.1, C43.+, L2.1, R10.1, R18.2, U5.D2 (VIN); also elsewhere on the board
VDD_POST_LC: C31.1, C33.1, L2.2, U7.5 (EN), U7.8 (IN)
VDRIVE: C44.+; also elsewhere on the board
VOUT-: C38.1, C41.2, C42.2, D1.A, L1.1, R12.1, U5.B2 (VOUT)
VSS_POST_LC: C30.1, C32.1, L1.2, U6.5 (EN), U6.8 (IN)

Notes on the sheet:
Ground Link

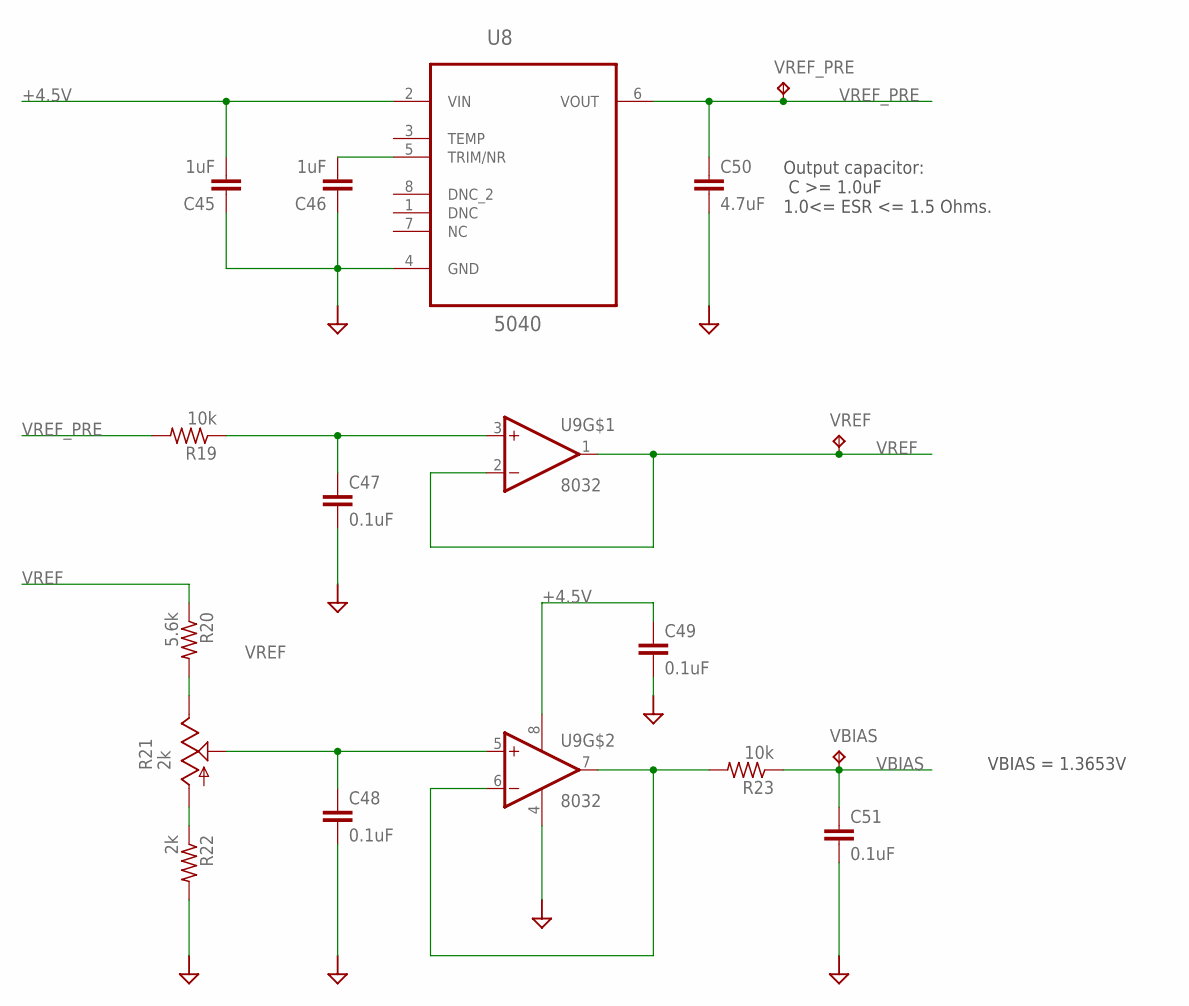
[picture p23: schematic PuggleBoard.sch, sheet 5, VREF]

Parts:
C45, C46: 1uF; 0603
C47, C48, C49, C51: 0.1uF; 0603
C50: 4.7uF; 1206
R19, R23: 10k; 0603
R20: 5.6k; 0603
R21: 2k; SM-42/43W
R22: 2k; 0603
U8: 5040; SOP65P490X110-8N
U9: 8032; SOP65P490X110-8N
VBIAS: TPB1,27; B1,27
VREF: TPB1,27; B1,27
VREF_PRE: TPB1,27; B1,27

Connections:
+4.5V: C45.2, C49.1, U8.2 (VIN), U9.8 (V+); also elsewhere on the board
GND: C45.1, C46.1, C47.2, C48.2, C49.2, C50.2, C51.2, R22.2, U8.4 (GND), U9.4 (V-); also elsewhere on the board
unnamed: C48.1, R21.2 (S), U9.5 (+IN)
unnamed: R21.1 (A), R22.1
unnamed: R23.2, U9.6 (-IN), U9.7 (OUT)
unnamed: R20.2, R21.3 (E)
unnamed: C47.1, R19.1, U9.3 (+IN)
unnamed: C46.2, U8.5 (TRIM/NR)
VBIAS: C51.1, R23.1, VBIAS.TP; also elsewhere on the board
VREF: R20.1, U9.1 (OUT), U9.2 (-IN), VREF.TP; also elsewhere on the board
VREF_PRE: C50.1, R19.2, U8.6 (VOUT), VREF_PRE.TP

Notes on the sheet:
Output capacitor: C >= 1.0uF 1.0<= ESR <= 1.5 Ohms.
VBIAS = 1.3653V

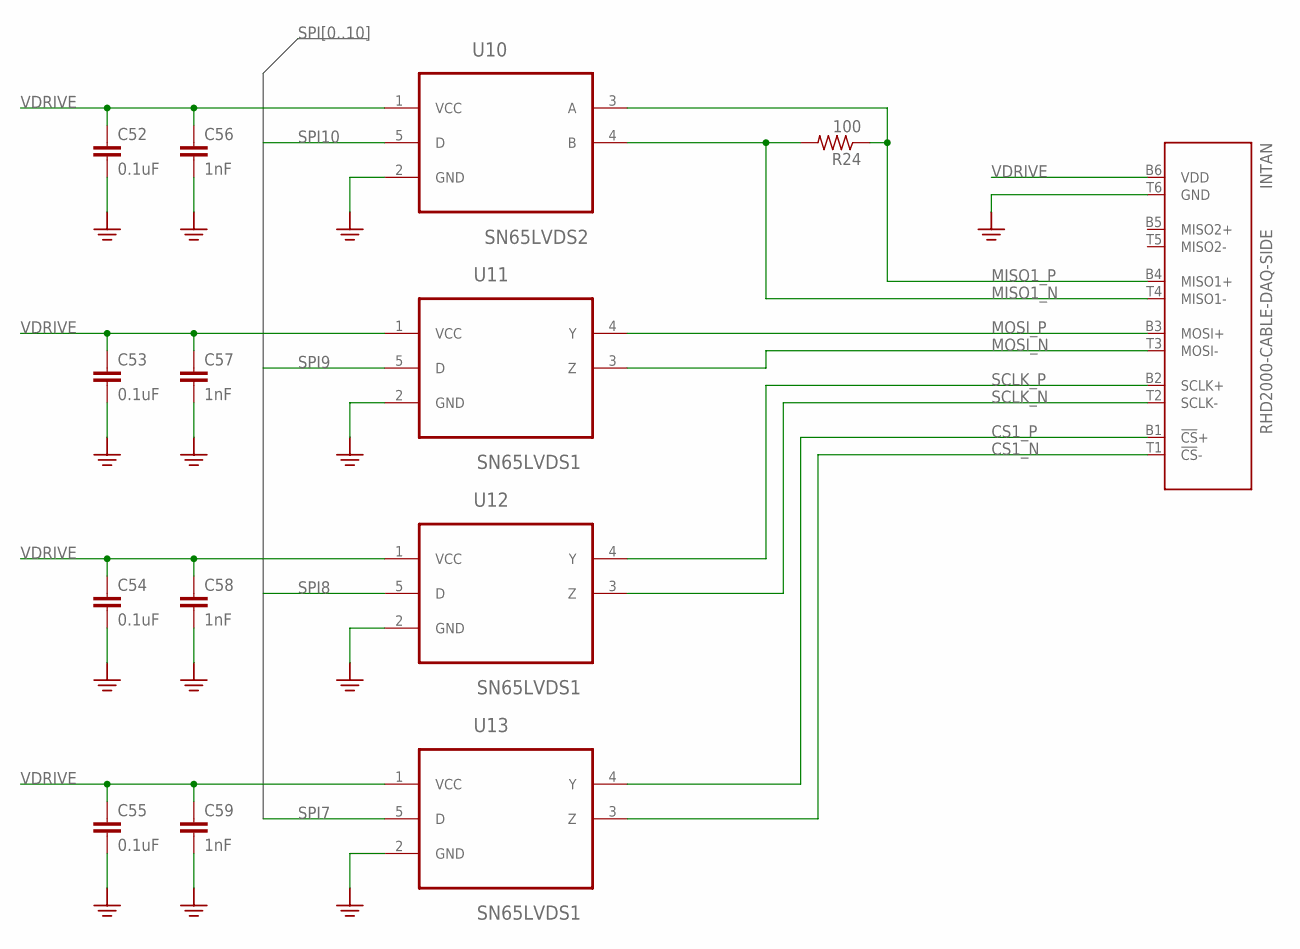
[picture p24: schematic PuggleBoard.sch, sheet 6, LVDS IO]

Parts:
C52, C53, C54, C55: 0.1uF; 0603
C56, C57, C58, C59: 1nF; 0603
INTAN: RHD2000-CABLE-DAQ-SIDE; OMNETICS_PZN-12-AA
R24: 100; 0603
U10: SN65LVDS2; SOT95P280X145-5N; DIGIKEY 296-6920-1-ND
U11, U12, U13: SN65LVDS1; SOT95P280X145-5N; DIGIKEY 296-6919-1-ND

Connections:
CS1_N: INTAN.T1 (!CS!-), U13.3 (Z)
CS1_P: INTAN.B1 (!CS!+), U13.4 (Y)
GND: C52.2, C53.2, C54.2, C55.2, C56.2, C57.2, C58.2, C59.2, INTAN.T6 (GND), U10.2 (GND), U11.2 (GND), U12.2 (GND), U13.2 (GND); also elsewhere on the board
MISO1_N: INTAN.T4 (MISO1-), R24.2, U10.4 (B)
MISO1_P: INTAN.B4 (MISO1+), R24.1, U10.3 (A)
MOSI_N: INTAN.T3 (MOSI-), U11.3 (Z)
MOSI_P: INTAN.B3 (MOSI+), U11.4 (Y)
SCLK_N: INTAN.T2 (SCLK-), U12.3 (Z)
SCLK_P: INTAN.B2 (SCLK+), U12.4 (Y)
SPI7: U13.5 (D); also elsewhere on the board
SPI8: U12.5 (D); also elsewhere on the board
SPI9: U11.5 (D); also elsewhere on the board
SPI10: U10.5 (D); also elsewhere on the board
VDRIVE: C52.1, C53.1, C54.1, C55.1, C56.1, C57.1, C58.1, C59.1, INTAN.B6 (VDD), U10.1 (VCC), U11.1 (VCC), U12.1 (VCC), U13.1 (VCC); also elsewhere on the board

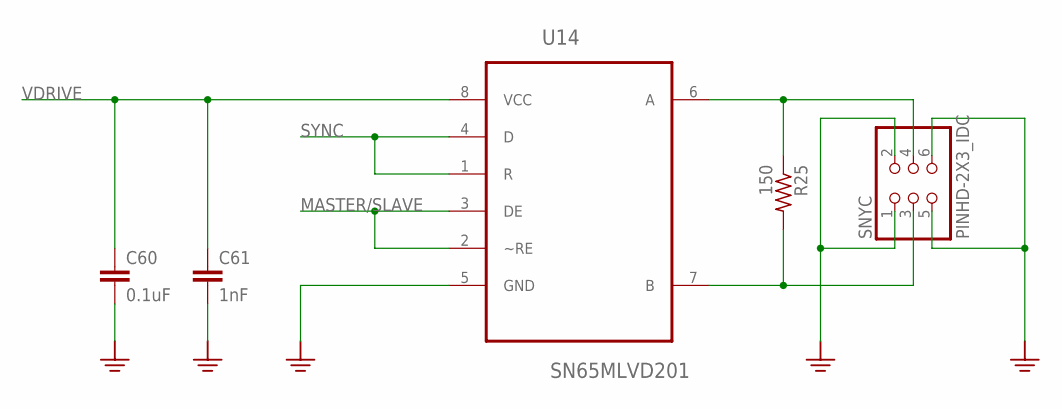
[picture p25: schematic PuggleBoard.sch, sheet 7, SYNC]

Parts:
C60: 0.1uF; 0603
C61: 1nF; 0603
R25: 150; 0603
SNYC: PINHD-2X3_IDC; 2X03_IDC
U14: SN65MLVD201; SOIC127P600X175-8N

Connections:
GND: C60.2, C61.2, SNYC.1, SNYC.2, SNYC.5, SNYC.6, U14.5 (GND); also elsewhere on the board
MASTER/SLAVE: U14.2 (~RE), U14.3 (DE); also elsewhere on the board
SYNC: U14.1 (R), U14.4 (D); also elsewhere on the board
SYNC_N: R25.2, SNYC.3, U14.7 (B)
SYNC_P: R25.1, SNYC.4, U14.6 (A)
VDRIVE: C60.1, C61.1, U14.8 (VCC); also elsewhere on the board

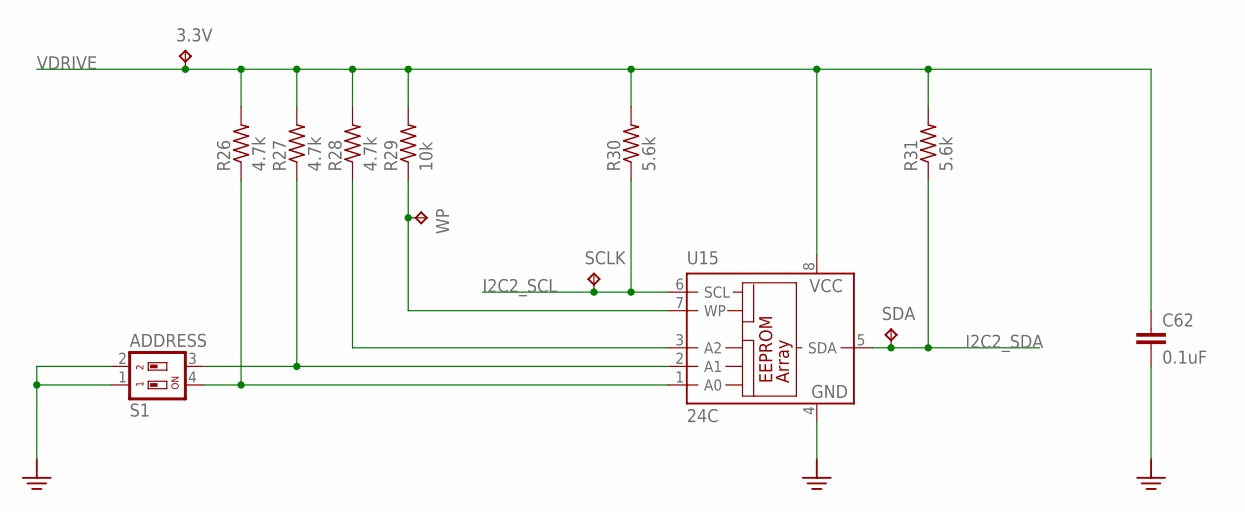
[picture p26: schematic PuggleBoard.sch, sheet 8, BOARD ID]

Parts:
3.3V: TPPAD1-17; P1-17
C62: 0.1uF; 0603
R26, R27, R28: 4.7k; 0603
R29: 10k; 0603
R30, R31: 5.6k; 0603
S1: ADDRESS; SMS-002
SCLK: TPB1,27; B1,27
SDA: TPB1,27; B1,27
U15: 24C; SO-08
WP: TPTP14SQ; TP14SQ

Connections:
GND: C62.2, S1.1, S1.2, U15.4 (GND); also elsewhere on the board
I2C2_SCL: R30.1, SCLK.TP, U15.6 (SCL); also elsewhere on the board
I2C2_SDA: R31.1, SDA.TP, U15.5 (SDA); also elsewhere on the board
unnamed: R26.1, S1.4, U15.1 (A0)
unnamed: R27.1, S1.3, U15.2 (A1)
unnamed: R28.1, U15.3 (A2)
unnamed: R29.1, U15.7 (WP), WP.TP
VDRIVE: 3.3V.TP, C62.1, R26.2, R27.2, R28.2, R29.2, R30.2, R31.2, U15.8 (VCC); also elsewhere on the board

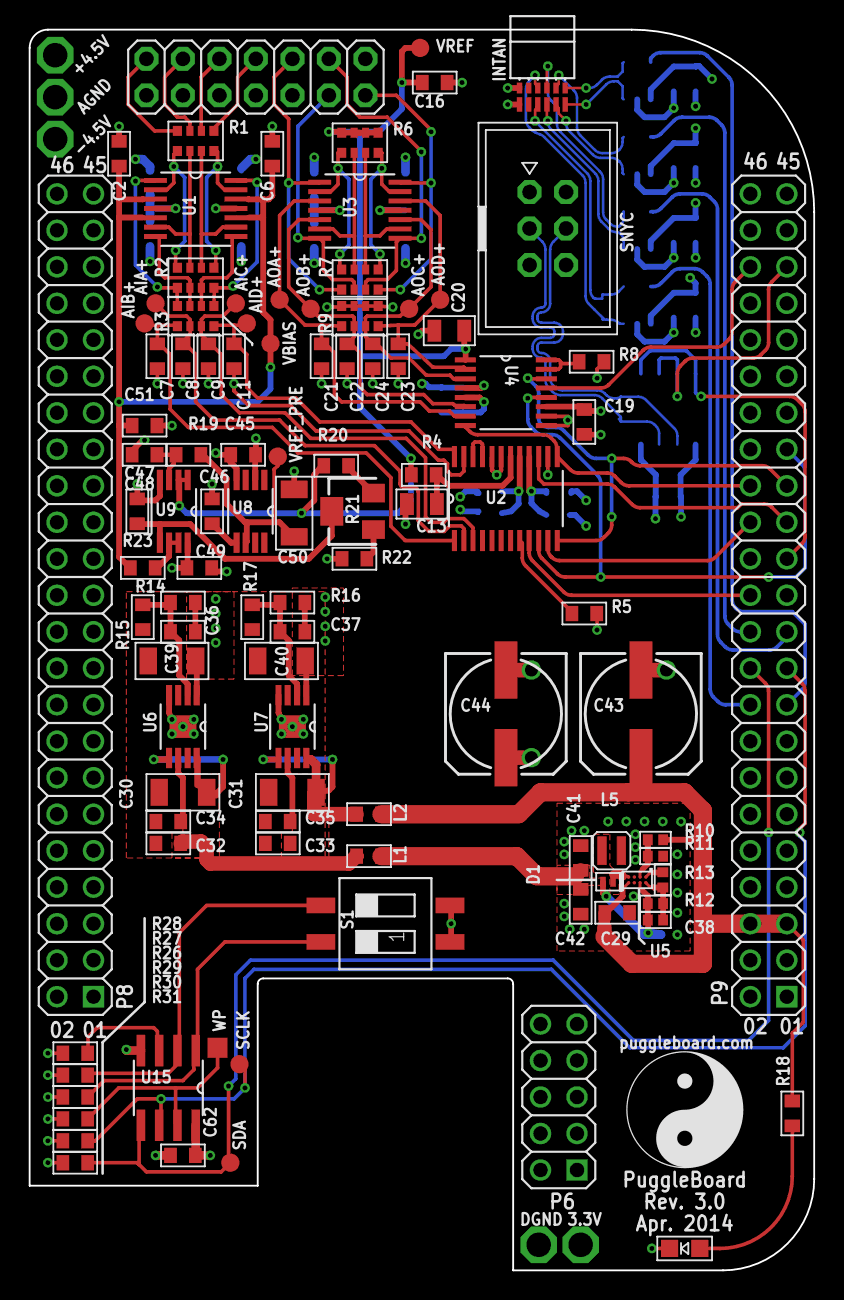
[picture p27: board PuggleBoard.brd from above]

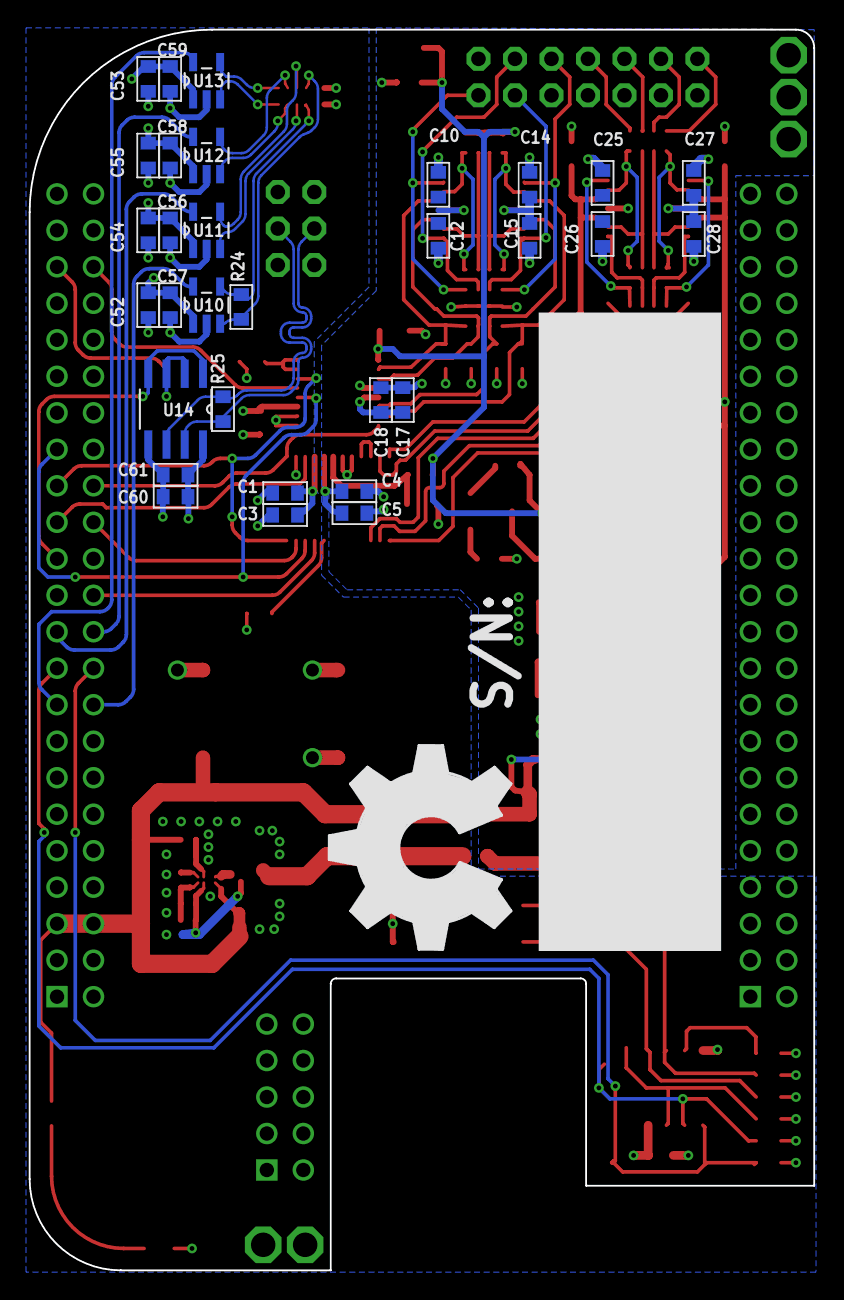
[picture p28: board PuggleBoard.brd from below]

Board: 4 copper layers, 54.6 x 86.4 mm, 139 parts (32 on the bottom side), 87 nets.

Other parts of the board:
U$1: PB-LOGO-NOSITE
U$2: OSHW_FILLX500_NOTEXT

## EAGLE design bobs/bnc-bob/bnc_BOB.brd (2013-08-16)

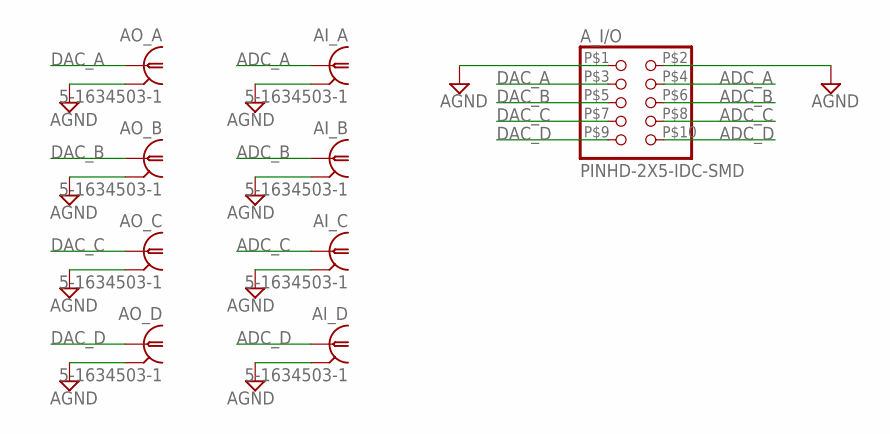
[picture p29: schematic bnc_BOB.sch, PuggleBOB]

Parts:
AI_A: 5-1634503-1; B35N61
AI_B: 5-1634503-1; B35N61
AI_C: 5-1634503-1; B35N61
AI_D: 5-1634503-1; B35N61
AO_A: 5-1634503-1; B35N61
AO_B: 5-1634503-1; B35N61
AO_C: 5-1634503-1; B35N61
AO_D: 5-1634503-1; B35N61
A_I/O: PINHD-2X5-IDC-SMD; 2X05-IDC-SMD

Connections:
ADC_A: AI_A.1, A_I/O.P$4 (4)
ADC_B: AI_B.1, A_I/O.P$6 (6)
ADC_C: AI_C.1, A_I/O.P$8 (8)
ADC_D: AI_D.1, A_I/O.P$10 (10)
AGND: AI_A.2, AI_A.3 (2), AI_A.4 (2), AI_A.5 (2), AI_B.2, AI_B.3 (2), AI_B.4 (2), AI_B.5 (2), AI_C.2, AI_C.3 (2), AI_C.4 (2), AI_C.5 (2), AI_D.2, AI_D.3 (2), AI_D.4 (2), AI_D.5 (2), AO_A.2, AO_A.3 (2), AO_A.4 (2), AO_A.5 (2), AO_B.2, AO_B.3 (2), AO_B.4 (2), AO_B.5 (2), AO_C.2, AO_C.3 (2), AO_C.4 (2), AO_C.5 (2), AO_D.2, AO_D.3 (2), AO_D.4 (2), AO_D.5 (2), A_I/O.P$1 (1), A_I/O.P$2 (2)
DAC_A: AO_A.1, A_I/O.P$3 (3)
DAC_B: AO_B.1, A_I/O.P$5 (5)
DAC_C: AO_C.1, A_I/O.P$7 (7)
DAC_D: AO_D.1, A_I/O.P$9 (9)

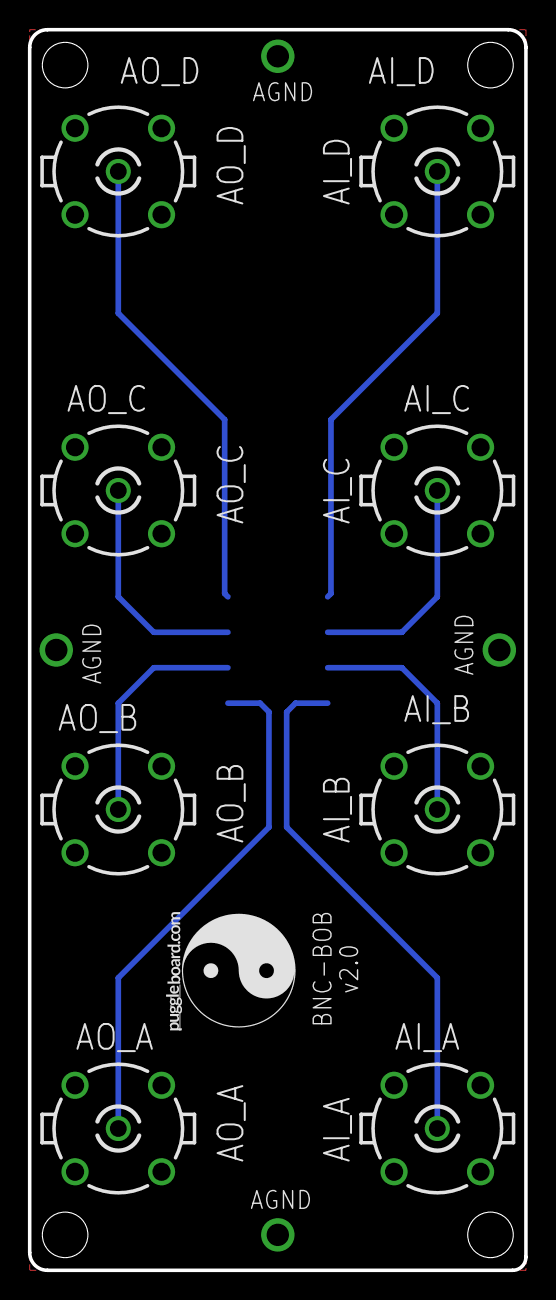
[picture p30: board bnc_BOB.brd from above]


Board: 2 copper layers, 35.6 x 88.9 mm, 11 parts (2 on the bottom side), 9 nets.

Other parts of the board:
U$1: PB-LOGO
U$2: OSHW_FILLX500_NOTEXT

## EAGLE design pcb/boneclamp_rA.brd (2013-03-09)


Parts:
U3: SN74ABT541BDW; SOIC127P1030X265-20N
U$1: BEAGLEBONE_OUTLINE; BEAGLEBONE_SHIELD

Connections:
AGND: U$1.1 (GND), U$1.2 (GND), U$1.47 (GND), U$1.48 (GND), U$1.89 (GND), U$1.90 (GND), U$1.91 (GND); also elsewhere on the board
AIN0: U$1.85 (AIN0)
BB_5V: U$1.53 (SYS_5V), U$1.54 (SYS_5V); also elsewhere on the board
DGND: U$1.92 (GND); also elsewhere on the board
I2C2_SCL: U$1.65 (I2C2_SCL); also elsewhere on the board
I2C2_SDA: U$1.66 (I2C2_SDA); also elsewhere on the board
VCC: U3.20 (VCC)
VDD_BB: U$1.51 (VDD_5V), U$1.52 (VDD_5V); also elsewhere on the board
VDRIVE: U$1.49 (VDD_3V3EXP), U$1.50 (VDD_3V3EXP); also elsewhere on the board

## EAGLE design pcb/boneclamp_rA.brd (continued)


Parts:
BCIO: F15-SHEILD; HDF15H
C1, C2, C3, C4: 1 uF; C0402
JP1, JP3: JP1E; JP1
JP2: JP2E; JP2
U1: AD7656YSTZ; QFP50P1200X1200X160-64N
U7: AD7682BCPZ; QFN50P400X400X100-21N

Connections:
AGND: BCIO.1, C1.2, C2.2, C3.2, C4.2, JP1.2, U1.32 (AGND), U1.37 (AGND_3), U1.38 (AGND_5), U1.43 (AGND_2), U1.44 (AGND_6), U1.49 (AGND_4), U1.52 (AGND_7), U1.53 (AGND_9), U1.57 (AGND_8), U1.59 (AGND_11); also elsewhere on the board
CONVST: U1.21 (CONVST_C), U1.22 (CONVST_B), U1.23 (CONVST_A)
DAC_A: BCIO.8; also elsewhere on the board
DAC_B: BCIO.9; also elsewhere on the board
DAC_C: BCIO.10; also elsewhere on the board
DAC_D: BCIO.11; also elsewhere on the board
DGND: JP2.3, U1.8 (DGND), U1.25 (DGND_2); also elsewhere on the board
DVCC: U1.26 (DVCC); also elsewhere on the board
unnamed: BCIO.2, U1.33 (V1)
unnamed: BCIO.3, U1.36 (V2)
unnamed: BCIO.4, U1.39 (V3)
unnamed: BCIO.5, U1.42 (V4)
unnamed: BCIO.6, U1.45 (V5)
unnamed: BCIO.7, U1.48 (V6)
unnamed: C2.1, U1.56 (REFCAPB)
unnamed: C1.1, U1.58 (REFCAPC)
unnamed: JP2.2, U1.27 (RANGE)
unnamed: C4.1, U1.34 (AVCC_8), U1.35 (AVCC), U1.40 (AVCC_5), U1.41 (AVCC_7), U1.46 (AVCC_2), U1.47 (AVCC_3), U1.50 (AVCC_6), U1.60 (AVCC_4)
unnamed: JP3.1, U1.51 (REFIN/REFOUT)
SGND: BCIO.P$1, BCIO.P$2, JP1.1
VDD: U1.31 (VDD), U7.20 (VDD); also elsewhere on the board
VDD_2: U7.1 (VDD_2)
VDRIVE: JP2.1; also elsewhere on the board
VIO: U7.15 (VIO)
VREF_2.5V: JP3.2; also elsewhere on the board
VSS: U1.30 (VSS); also elsewhere on the board


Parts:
C15, C16, C17, C18: C-EUC0603; C0603
JP4: JP1E; JP1
R1, R2, R3, R4: R-US_R0603; R0603
SJ1, SJ2, SJ3: SJ
TP1, TP2, TP3, TP4: TPB1,27; B1,27
U2: AD5754RBREZ; SOP65P640X120-25N
U$42: AD5686RARUZ; MO-153-AB

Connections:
AGND: C16.2, C17.2, C18.2, R2.1, R3.1, R4.1; also elsewhere on the board
DAC_A: C18.1, R4.2, TP1.TP, U2.3 (VOUTA); also elsewhere on the board
DAC_B: C17.1, R3.2, TP2.TP, U2.4 (VOUTB); also elsewhere on the board
DAC_C: C16.1, R2.2, TP3.TP, U2.23 (VOUTC); also elsewhere on the board
DAC_D: C15.1, R1.2, TP4.TP, U2.22 (VOUTD); also elsewhere on the board
DVCC: U2.14 (DVCC); also elsewhere on the board
EPAD: U2.25 (EPAD)
unnamed: SJ1.1, U2.16 (SDO)
unnamed: SJ2.2, SJ3.2, U2.9 (SDIN)
unnamed: C15.2, R1.1
unnamed: JP4.1, U2.17 (REFIN/REFOUT)
SDIN_BB: SJ2.1
SDIN_DC: SJ3.1
SDO_DC: SJ1.2
VDD: U2.24 (AVDD), U$42.5 (VDD); also elsewhere on the board
VREF_2.5V: JP4.2; also elsewhere on the board
VSS: U2.1 (AVSS); also elsewhere on the board


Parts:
C22: 0.1uF; C0603
IC1: 24C; SO-08
R6, R10: 5.6k; R0603
R7, R8, R9: 4.75k; R0603
R11: 10k; R0603
S1: SWS002; SMS-002
SJ5: SJ

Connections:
DGND: C22.2, IC1.4 (GND), S1.3, S1.4; also elsewhere on the board
I2C2_SCL: IC1.6 (SCL), R10.1; also elsewhere on the board
I2C2_SDA: IC1.5 (SDA), R6.1; also elsewhere on the board
unnamed: IC1.1 (A0), R7.1, R8.1, S1.1
unnamed: IC1.2 (A1), S1.2
unnamed: IC1.3 (A2), R9.1
unnamed: IC1.7 (WP), SJ5.1
unnamed: R11.1, SJ5.2
VDRIVE: C22.1, IC1.8 (VCC), R6.2, R7.2, R8.2, R9.2, R10.2, R11.2; also elsewhere on the board


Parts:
C5, C8, C10, C13, C19, C20: 10uF; C1206
C6, C7, C9, C11, C12, C14: 0.1uF; C0603
SJ4: SJ
U4, U5: ADP3303ARZ-5; SOIC127P600X175-8N
U$26: LM1085; TO263-3
U$28: SCREW3

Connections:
+12V: C19.1, U$26.3 (IN)
-12V: U$28.P$3
AGND: C5.2, C6.2, C9.2, C10.2, SJ4.1, U4.4 (GND), U5.4 (GND); also elsewhere on the board
AVCC: C7.1, C9.1, C10.1, U4.1 (OUT_2), U4.2 (OUT)
BB_5V: C5.1, C6.1, C8.1, C11.1, U4.5 (~SD), U4.7 (IN), U4.8 (IN_2), U5.5 (~SD), U5.7 (IN), U5.8 (IN_2); also elsewhere on the board
DGND: C8.2, C11.2, C13.2, C14.2, C19.2, C20.2, SJ4.2, U$26.1 (ADJ); also elsewhere on the board
DVCC: C12.1, C13.1, C14.1, U5.1 (OUT_2), U5.2 (OUT); also elsewhere on the board
unnamed: C12.2, U5.3 (NR)
unnamed: C7.2, U4.3 (NR)
PGND: U$28.P$2
VDD_BB: C20.1, U$26.2 (OUT), U$26.TAB (OUT); also elsewhere on the board


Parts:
C23: 10uF; C1206
C24, C26, C27: 0.1uF; C0603
JP5: JP2E; JP2
JP6: JP1E; JP1
TP5: TPB1,27; B1,27
U6: ADR431BRZ; SOIC127P600X175-8N

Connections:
AGND: C23.2, C24.2, C26.2, U6.4 (GND); also elsewhere on the board
unnamed: C26.1, U6.1 (TP_2)
VDD: C23.1, C24.1, U6.2 (VIN); also elsewhere on the board
VREF_2.5V: JP5.2; also elsewhere on the board
VREF_OUT: C27.1, JP5.3, JP6.2, TP5.TP, U6.6 (VOUT)

Board: 4 copper layers, 65 parts (0 on the bottom side), 43 nets, no tracks yet.

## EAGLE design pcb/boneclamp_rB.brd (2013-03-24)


Board: 4 copper layers, 160.0 x 100.0 mm, 136 parts (0 on the bottom side), 59 nets, no tracks yet.

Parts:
C1, C3, C10, C11, C20, C44, C45, C53, C54: 10uF; C0805
C2, C4, C12, C13, C14, C19, C21, C40, C41, C46, C47, C48, C49, C50, C55, C56: 0.1uF; C0805
C5, C8, C9: 1uF; C0603
C6, C29: 10nF; C0603
C7, C23: 10uF; C0603
C15, C16, C17, C18: C0805
C22, C26: 0.1uF; C0603
C24: 22nF; C0603
C25, C28, C36, C37, C38, C39: C025-025X050
C27: 4.7nF; C0603
C30, C31, C32, C33: 4.7uF; C0603
C34: 0.22uF; C0603
C35: 10pF; C0603
C42, C43, C51, C52: 2.7nF; C0805
D1: DO-219AB
IC1: 24C; SO-08
JP1: JP1
JP5: PINHD-2X5/90; 2X05/90
L1: 4.7uH; L4012M
R1, R2, R3, R4: R0805
R5: 100k; R0603
R6, R10: 5.6k; R0603
R7, R8, R9: 4.75k; R0603
R11: 10k; R0603
R12: 750; R0603
R13: 150k; R0603
R14: 1k; R0805
R15, R16: 10k,1%; R0805
R17, R18, R39, R40, R41, R42: 10k; R0805
R19: 6.937k; 0204V
R20, R22: 10k; 0204V
R21: 6.66k; 0204V
R23, R24, R25, R26, R27, R28, R29, R30: 0204V
R31, R38, R43, R44: 0.1k; R0805
R32, R33, R36, R37: 33; R0603
R34, R35, R45, R46: 590; R0603
S2: SWS003; SMS-003
SJ1, SJ2, SJ3, SJ4, SJ6, SJ7, SJ8: SJ
TP1, TP2, TP3, TP4, TP5, TP6, TP7: TPB1,27; B1,27
U1: AD8032ARZ-REEL7; SOIC127P600X175-8N
U2: LT1964ES5-5TRMPBF; SOT95P280X100-5N
U3, U5, U9, U10, U11: ADA4841-2YRZ; SOIC127P600X175-8N
U4: TLV70245DBVT; SOT95P280X110-5N
U6: AD713JRZ-16; SOIC127P1032X265-16N
U7: AD7682BCPZ; QFN50P400X400X100-21N
U8: TPS63700DRCT; SON50P300X300X100-11N
U$1: BEAGLEBONE_OUTLINE; BEAGLEBONE_SHIELD
U$42: AD5686; MO-153-AB
U$77: ADS8343; SOP63P500X150-16N

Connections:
ADC_A: JP5.4, U9.3, U10.3
ADC_B: JP5.6, U9.5, U10.5
ADC_C: JP5.8, U5.3, U11.3
ADC_D: JP5.10, U5.5, U11.5
AGND: C1.2, C2.2, C3.2, C5.2, C6.2, C7.2, C8.2, C9.2, C10.2, C11.2, C12.2, C13.2, C14.2, C16.2, C17.2, C18.2, C19.2, C20.2, C21.2, C23.2, C24.2, C26.2, C27.2, C29.2, C30.2, C31.2, C32.2, C33.2, C34.2, C40.2, C41.2, C42.2, C43.2, C44.1, C45.2, C46.2, C47.2, C48.2, C49.2, C50.2, C51.2, C52.2, C53.1, C54.2, C55.2, C56.2, L1.2, R2.1, R3.1, R4.1, R16.2, SJ4.1, U1.4, U2.1, U4.2, U7.4, U7.5, U7.21, U8.2, U8.7, U8.11, U$1.90, U$42.4, U$42.10, U$42.16
DAC_LDAC: R18.1, U$42.9
DAC_RST: R17.1, U$42.15
DGND: C22.2, IC1.4, S2.4, S2.5, S2.6, SJ4.2, U$1.92
GND: C25.1, C28.1, C36.1, C38.1, C39.1, U6.8, U6.9, U$1.1, U$1.2, U$1.47, U$1.48, U$1.89, U$1.91, U$77.10, U$77.11
I2C2_SCL: IC1.6, R10.1, TP5.TP, U$1.65
I2C2_SDA: IC1.5, R6.1, TP7.TP, U$1.66
unnamed: R37.2, R45.1, U5.6, U5.7
unnamed: R33.2, R34.1, U9.6, U9.7
unnamed: R26.2, R30.1, U6.14
unnamed: C1.1, R15.2, R16.1, U1.5
unnamed: R36.2, R46.1, U5.1, U5.2
unnamed: SJ1.1, U$42.8
unnamed: SJ2.2, SJ3.2, U$42.14
unnamed: SJ7.2, SJ8.2, U7.12
unnamed: IC1.1, R7.1, S2.1
unnamed: C6.1, U2.3
unnamed: C15.2, R1.1
unnamed: IC1.2, R8.1, S2.2
unnamed: IC1.3, R9.1, S2.3
unnamed: R32.2, R35.1, U9.1, U9.2
unnamed: IC1.7, JP1.2
unnamed: JP1.1, R11.1
unnamed: C26.1, R5.2, U8.3, U8.4
unnamed: C27.1, U8.1
unnamed: D1.P$1, L1.1, U8.6
unnamed: C11.1, R14.2, U7.2
unnamed: C10.1, R14.1, U1.3
unnamed: C35.1, R12.2, R13.1, U8.9
unnamed: C34.1, R13.2, U8.10
unnamed: C14.1, U7.3
unnamed: R25.2, R29.1, U6.12
unnamed: C38.2, R21.1, R22.2, U3.5
unnamed: C28.2, R19.1, R20.2, U3.3
unnamed: R24.2, R28.1, U6.5
unnamed: R23.2, R27.1, U6.3
unnamed: C25.2, R20.1
VBIAS: C46.1, C47.1, C48.1, C55.1, C56.1, R34.2, R35.2, R45.2, R46.2, U1.6, U1.7
VBIAS_DOWN: C39.2, U3.6, U3.7, U6.2, U6.6, U6.11, U6.15
VBIAS_UP: C36.2, R31.2, R38.2, R39.1, R39.2, R40.1, R40.2, R41.1, R41.2, R42.1, R42.2, R43.2, R44.2, U3.1, U3.2, U10.2, U10.6, U11.2, U11.6
VCC: U$77.1, U$77.9
VDD: C2.1, C3.1, C9.1, C13.1, C19.1, C20.1, C40.1, C45.1, C49.1, C54.1, R19.2, U1.8, U3.8, U4.5, U5.8, U6.4, U7.1, U7.20, U9.8, U10.8, U11.8, U$42.5
VDD_5V: C8.1, C23.1, C24.1, R5.1, U4.1, U4.3, U8.5, U$1.51, U$1.52
VDRIVE: C4.1, C12.1, C22.1, IC1.8, R6.2, R7.2, R8.2, R9.2, R10.2, R11.2, R17.2, R18.2, TP6.TP, U7.15, U$1.49, U$1.50, U$42.11
VREF: C21.1, R15.1, U1.1, U1.2, U$42.1
VSS: C7.1, C41.1, C44.2, C50.1, C53.2, R21.2, U2.5, U3.4, U5.4, U6.13, U9.4, U10.4, U11.4
_ADC_A: C42.1, R32.1, R38.1, U7.16, U10.1
_ADC_B: C43.1, R31.1, R33.1, U7.18, U10.7
_ADC_C: C51.1, R36.1, R43.1, U7.7, U11.1
_ADC_D: C52.1, R37.1, R44.1, U7.9, U11.7
_DAC_A: C15.1, R1.2, R23.1, R30.2, TP4.TP, U6.16, U$42.3
_DAC_B: C16.1, R2.2, R26.1, R27.2, TP3.TP, U6.1, U$42.2
_DAC_C: C17.1, R3.2, R25.1, R28.2, TP2.TP, U6.7, U$42.6
_DAC_D: C18.1, R4.2, R24.1, R29.2, TP1.TP, U6.10, U$42.7
_VSS: C5.1, C29.1, C30.1, C31.1, C32.1, C33.1, C35.2, D1.P$2, R12.1, U2.2, U2.4, U8.8

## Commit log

2013-02-24 Renamed the pcb folder to be more in line with other directory names
    [boneclamp.brd, boneclamp.sch]
2013-02-24 Started working through the basic wiring on the schematic, connectrating on grounds, power, and analog IO
    [boneclamp.brd, boneclamp.sch]
2013-02-25 Added optional compensation comoponents and test points to DAC output lines. Added a right angle 0.1 inch pitch header for outside power input.
    [boneclamp.brd, boneclamp.sch]
2013-02-27 I put an anti-aliasing filter design tool, provided by TI, into the PCB folder. The stop frequency (the frequency at which the attenuation is equal to the noise floor of the ADC (NOT the -3 dB point)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
    [anti-aliasing-design-tool.xls]
2013-03-03 Found a good regulator for powering the BB using the +/- 6 to 12 volt rails required to use the boneclamp. Updated schematic and added data sheet to data-sheets folder
    [anti-aliasing-design-tool.xls, boneclamp.brd, boneclamp.sch]
2013-03-03 Started and examples folder containing information about good capes produced by other people
    [BeagleBone-Battery-RevA-allegro.brd, BeagleBone-Battery-RevA-bom.xls, BeagleBone-Battery-RevA-schematic.dsn]
2013-03-03 Added EEPROM to the I2C2bus to follow standard daughter board device ID requirements
    [boneclamp.brd, boneclamp.sch]
2013-03-03 Added external 2.5 volt references for DAC and ADC. This circuit needs a buffer option which can be feed into the 3 position jumper.
    [boneclamp.brd, boneclamp.sch]
2013-03-09 Added new data sheets. Started a second pcb layout for new DAC/ADC unipolar solutions.
    [boneclamp.brd, boneclamp.sch, boneclamp_rB.brd, boneclamp_rB.sch]
2013-03-09 More changes to circuit
    [boneclamp_rB.brd, boneclamp_rB.sch]
2013-03-09 Renamed the old boneclamp schematic and board
    [boneclamp_rA.brd, boneclamp_rA.sch]
2013-03-09 Worked a bit on the schematic
    [boneclamp_rB.brd, boneclamp_rB.sch]
2013-03-10 Wired the DC-DC inverter
    [boneclamp_rB.brd, boneclamp_rB.sch]
2013-03-10 Added negative LDO regulator
    [boneclamp_rB.brd, boneclamp_rB.sch]
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2013-03-10 Minor schematic edit
    [boneclamp_rB.brd, boneclamp_rB.sch]
2013-03-11 Added data sheets for the smd-to-dip adapters we will use. Minor changes to schematic
    [boneclamp_rB.brd, boneclamp_rB.sch]
2013-03-12 Finished power supply circuits on schematic. Updated BOM and added new data sheets.
    [boneclamp_rB.brd, boneclamp_rB.sch]
2013-03-13 Updated adafruit library with 2X5 0.1 inch pitch header, which we will use for I/O on the BC. Added that to the schematic
    [boneclamp_rB.brd, boneclamp_rB.sch]
2013-03-13 Finished basic ADC module
    [boneclamp_rB.brd, boneclamp_rB.sch]
2013-03-14 Added buffered VREF divider, which feeds back into ADC to get bipolar input swing.
    [boneclamp_rB.brd, boneclamp_rB.sch]
2013-03-14 Finished digital input to DAC
    [boneclamp_rB.brd, boneclamp_rB.sch]
2013-03-15 Minor fixed to EEPROM circuit and ADC VREF buffer. Stephano, don't kill me.
    [boneclamp_rB.brd, boneclamp_rB.sch]
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2013-03-17 Added another example cape, this one has the exact dimensions we are interested in and is well documented.
    [BeagleBone-Audio-RevA-bom.xls, BeagleBone-Audio-RevA-schematic.dsn, BeagleBone_Battery_Rev A_ncdrill-1-2.drl, BeagleBone_Battery_Rev A_netlist_allegro.xls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]
2013-03-17 Minor edit
    [boneclamp_rB.brd, boneclamp_rB.sch]
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2013-03-18 Added p6 to the schematic of the BB, update the BC shematic and board
    [boneclamp_rB.brd, boneclamp_rB.sch]
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2013-03-23 Fixed the input biasing scheme. The op-amps we are using require -0.25 to 5.2 volt supply range to push the inputs into the 0 to 4.096 range required by the ADC. This means that our positive rail is 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
    [boneclamp_rB.brd, boneclamp_rB.sch]
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2013-03-25 Added yet another option to explore for the ADC. I need to make some calls to find out what the best option is. There is always something wrong with any particular choice.
    [boneclamp_rC.brd, boneclamp_rC.sch]
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2013-03-29 Minor fixes to voltage bias followers
    [boneclamp_rC.brd, boneclamp_rC.sch]
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2013-04-04 Fixed DAC output bias
    Biased DAC output, other minor schematic changes
    [boneclamp_rC.brd, boneclamp_rC.sch]
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2013-04-06 Replaced negative LDO with the MAX1735.
    [boneclamp_rC.brd, boneclamp_rC.sch]
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2013-04-20 Started getting rid of signal tag symbols, take too much room and cause problems with automatic component renumbering.
    [boneclamp_rC.brd, boneclamp_rC.sch]
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2013-04-20 Minor fix.
    [boneclamp_rC.brd, boneclamp_rC.sch]
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2013-05-04 Fixed the ground planes.
    [boneclamp_rC.brd, boneclamp_rC.sch]
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2013-05-12 Fixed some random problems with the silkscreen.
    [boneclamp_rC.brd, boneclamp_rC.sch]
2013-05-12 More minor silkscreen issues. Started drawing logo.
    [boneclamp_rC.brd]
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2013-05-19 Fixed the ribbon cable mapping to take into account reflective symmetry.
    [PuggleBOB.brd, PuggleBOB.sch, PuggleBoard.brd, PuggleBoard.sch]
2013-05-19 Fixed the GPIO pin out to match pins available to the PRU in MODE6
    [PuggleBoard.brd, PuggleBoard.sch]
2013-05-20 Almost done actually fixing GPIO mapping for PRU1
    [PuggleBoard.brd, PuggleBoard.sch]
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2013-05-20 Fixed BOMs
    [puggleBOB_BOM.csv, puggleBOB_BOM_DK.csv]
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2013-05-28 Fixed BOM for v1.0
    [puggleboard_BOM.csv, puggleboard_BOM_DK.csv]
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2013-07-21 Working through v1.0 fixes.
    [PuggleBoard.brd, PuggleBoard.sch]
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2013-08-06 Replaced swiching inverter with uModule. Removed external power option.
    [PuggleBoard.brd, PuggleBoard.sch]
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2013-08-07 Intial layout complete. Time to clean up DRC errors.
    [PuggleBoard.brd, PuggleBoard.sch]
2013-08-07 DRC correction finished. Doing silkscreen.
    [PuggleBoard.brd, PuggleBoard.sch]
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2013-08-07 Fixed some silk-screen issues.
    [PuggleBoard.brd]
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2013-08-10 Fixed logo and made a part in the puggleboard library so that it is easy to add. Many minor changes to both boards. Should be just about ready to go.
    [PuggleBoard.brd, PuggleBoard.sch, lvds-omnetics_BOB.brd, lvds-omnetics_BOB.sch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]
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2013-08-18 Almost done with DK BOMs. Still a few problems: (1) There are some parts (e.g. 46 pin headers) that do not appear as individual components since they are included with the BB device that need to be m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
    [lvds-omnetics_BOB.brd, puggleBOB_BOM.csv, puggleBOB_BOM_DK.csv, ttl-bob.brd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]
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2013-09-26 Fixed a couple previous issues with v2.0 board and added a third.
    [PuggleBoard.brd, PuggleBoard.sch]
2013-09-26 Fixed issue three in board/doc/notes_2v0-assembly.
    [PuggleBoard.brd, PuggleBoard.sch]
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2013-10-12 Modified board to take care of issues with eMMC pin conflicts.
    [PuggleBoard.brd, PuggleBoard.sch]
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2013-10-19 Some minor changes to address v2.0 issues.
    [PuggleBoard.brd]
2013-10-27 Fixed several problems in grounding scheme causing digital/analog interference.
    [PuggleBoard.brd, PuggleBoard.sch]
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2013-11-19 Fixed V_Ref bypass cap for DAC.
    [PuggleBoard.brd, PuggleBoard.sch]
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2014-01-05 Started fixing issues with r2.1 build. Fixed up silkscreen to make it more legible. Fixed issue with voltage ref miswiring.
    [PuggleBoard.brd, PuggleBoard.sch]
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2014-04-21 Starting revisions to create r3.0 of the board. Fixed most of the schematic. Added LVDS circuit.
    [PuggleBoard.brd, PuggleBoard.sch]
2014-04-21 Fixed a couple more op-amp symbols.
    [PuggleBoard.brd, PuggleBoard.sch]
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2014-04-22 Replaced several resistor banks with match resistor arrays.
    [PuggleBoard.brd, PuggleBoard.sch]
2014-04-24 Added additional ferrite chip on +5V rail from BB, fixed some other minor stuff.
    [PuggleBoard.brd, PuggleBoard.sch]
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2014-04-30 Fixed the flipped pin on the MISO LVDS module that Yogi found.
    [PuggleBoard.brd, PuggleBoard.sch]
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2014-05-21 Fixed a few DRC errors.
    [PuggleBoard.brd, PuggleBoard.sch]
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2014-05-22 Routing complete. Many ERC and DRC fixes.
    [PuggleBoard.brd, PuggleBoard.sch]
2014-05-22 Board is ready for Edgar to look at. There is one strange DRC error, but that can be resolved later. Also, silk screens are a mess, but Edgar can see the layout at least.
    [PuggleBoard.brd, PuggleBoard.sch]
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2014-05-29 Minor improvements. Reverted back to old board shape since we are not using the upper right corner for anything.
    [PuggleBoard.brd, PuggleBoard.sch]
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2014-05-30 Finished top layer silkscreen. Moved ground points on decoupling capacitors to beneath the pad. This will result in a DRC error, but I saw an analog devices eval board doing this. It makes sense and 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
    [PuggleBoard.brd, PuggleBoard.sch]
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2014-06-23 Fixed a couple minor issues found while making the boards.
    [PuggleBoard.brd, PuggleBoard.sch]
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2014-07-29 fixed issue with DAC channel pinout; channel numbers did not map to actual DAC output (e.g. requested output on channel A but came out on C).
    [PuggleBoard.brd, PuggleBoard.sch]
